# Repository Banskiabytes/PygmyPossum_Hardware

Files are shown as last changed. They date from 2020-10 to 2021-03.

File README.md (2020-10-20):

[][contributors-url]
[][forks-url]
[][stars-url]
[][issues-url]
[][license-url]
[][linkedin-url]

<!-- PROJECT LOGO -->
<br />
<p align="center">
  <a href="https://github.com/tomevison/">
    
  </a>

  <h3 align="center">The Pygmy Possum</h3>
  <p align="center">PIR sensor for camera traps</p>
</p>

<!-- TABLE OF CONTENTS -->
## Table of Contents

* [About the Project](#about-the-project)
* [Built With](#built-with)
* [Usage](#usage)
* [License](#license)
* [Contact](#contact)

<!-- ABOUT THE PROJECT -->
## About The Project

## Built With
#### Software:
* [KiCAD]

<!-- USAGE EXAMPLES -->
## Usage

Set the DIP switches on the front of the board to select your pre-programmed package. There are 8 pre-progammed packages in total. Each package contains a value for:
* Number of Shots to take after a Event
* Time Between Shots
* Minimum time between Events

<!-- LICENSE -->
## License

Distributed under the MIT License. See `LICENSE` for more information.

<!-- CONTACT -->
## Contact

* Tom Evison - tom@evisonengineering.com.au
* James Lidsey - james.lidsey93@gmail.com

<!-- MARKDOWN LINKS & IMAGES -->
<!-- https://www.markdownguide.org/basic-syntax/#reference-style-links -->
[contributors-shield]: https://img.shields.io/github/contributors/tomevison/repo.svg?style=flat-square
[contributors-url]: https://github.com/tomevison/PYGMY/graphs/contributors
[forks-shield]: https://img.shields.io/github/forks/tomevison/repo.svg?style=flat-square
[forks-url]: https://github.com/tomevison/repo/network/members
[stars-shield]: https://img.shields.io/github/stars/tomevison/repo.svg?style=flat-square
[stars-url]: https://github.com/tomevison/repo/stargazers
[issues-shield]: https://img.shields.io/github/issues/tomevison/repo.svg?style=flat-square
[issues-url]: https://github.com/EmbeddedEnvironmental/PygmyPossum_Firmware/issues
[license-shield]: https://img.shields.io/github/license/tomevison/repo.svg?style=flat-square
[license-url]: https://github.com/EmbeddedEnvironmental/PygmyPossum_Firmware/blob/master/LICENSE
[linkedin-shield]: https://img.shields.io/badge/-LinkedIn-black.svg?style=flat-square&logo=linkedin&colorB=555
[linkedin-url]: https://www.linkedin.com/in/thomas-evison-87b27073/# Hardware

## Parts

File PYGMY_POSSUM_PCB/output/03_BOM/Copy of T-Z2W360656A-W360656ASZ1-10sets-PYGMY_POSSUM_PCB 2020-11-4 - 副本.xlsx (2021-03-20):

PYGMY POSSUM v1.1 Build Of Materials
Date: | 2020-11-04
Ref | Value | Part | Footprint | Description | LCSC | Manufacturer | MPN | Package | Type | Part PCBWay Will Supply | Unit Price 10sets | Total Price | PCBWay Comments | Tom Comments
C1 | 0.1uF | Device:C_Small | Capacitor_SMD:C_0603_1608Metric | Unpolarized capacitor, small symbol | C14663 |  |  | 603 | SMD | CC0603KRX7R9BB104 | $0.052 | $0.525
C2 | 10pF | Device:C_Small | Capacitor_SMD:C_0603_1608Metric | Unpolarized capacitor, small symbol | C1634 |  |  | 603 | SMD | CL10C100JB8NNNC | $0.032 | $0.315
C3 | 10pF | Device:C_Small | Capacitor_SMD:C_0603_1608Metric | Unpolarized capacitor, small symbol | C1634 |  |  | 603 | SMD | CL10C100JB8NNNC | $0.032 | $0.315
C4 | CP10u | Device:CP | Capacitor_SMD:CP_Elec_4x3.9 | Polarized capacitor | C134721 |  |  | SMD-ECAP-4x5.3 | SMD | VE-100M1ETR-0405 | $0.210 | $2.100
C5 | CP10u | Device:CP | Capacitor_SMD:CP_Elec_4x3.9 | Polarized capacitor | C134721 |  |  | SMD-ECAP-4x5.3 | SMD | VE-100M1ETR-0405 | $0.210 | $2.100
C6 | 0.1uF | Device:C | Capacitor_SMD:C_0603_1608Metric | Unpolarized capacitor | C14663 |  |  | 603 | SMD | CC0603KRX7R9BB104 | $0.052 | $0.525
D3 | BAT60B | Diode:BAT60A | Diode_SMD:D_SOD-323 | 10V 3A High Current Recitifier Schottky Diode, SOD-323 | C514095 |  |  | SOD-323 | SMD | BAT60B | $0.105 | $1.050
J2 | AudioJack | Connector:AudioJack3 | Connector_Audio:Jack_3.5mm_CUI_SJ-3523-SMT_Horizontal | Audio Jack, 3 Poles (Stereo / TRS) |  | CUI Devices | SJ-3523-SMT-TR |  | SMD |  |  |  |  | This part has been updated (19/11/2020)
J3 | USB_B_Micro | Connector:USB_B_Micro | Connector_USB:USB_Micro-B_Molex-105017-0001 | USB Micro Type B connector |  | Molex | 105017-0001 |  | PTH / SMD | 105017-0001 | $0.945 | $9.450 | 5-7work days
Q1 | 2N7002 | Transistor_FET:2N7002 | Package_TO_SOT_SMD:SOT-23 | 0.115A Id, 60V Vds, N-Channel MOSFET, SOT-23 | C8545 | Changjiang Electronics Tech (CJ) | 2N7002 | SOT-23 | SMD | 2N7002 | $0.105 | $1.050
Q2 | 2N7002 | Transistor_FET:2N7002 | Package_TO_SOT_SMD:SOT-23 | 0.115A Id, 60V Vds, N-Channel MOSFET, SOT-23 | C8545 | Changjiang Electronics Tech (CJ) | 2N7002 | SOT-23 | SMD | 2N7002 | $0.105 | $1.050
Q3 | AO3401A | Transistor_FET:AO3401A | Package_TO_SOT_SMD:SOT-23 | -4.0A Id, -30V Vds, P-Channel MOSFET, SOT-23 | C15127 | Alpha & Omega Semicon | AO3401A | SOT-23 | SMD | AO3401A | $0.210 | $2.100
Q4 | AO3401A | Transistor_FET:AO3401A | Package_TO_SOT_SMD:SOT-23 | -4.0A Id, -30V Vds, P-Channel MOSFET, SOT-23 | C15127 | Alpha & Omega Semicon | AO3401A | SOT-23 | SMD | AO3401A | $0.210 | $2.100
Q5 | 2N7002 | Transistor_FET:2N7002 | Package_TO_SOT_SMD:SOT-23 | 0.115A Id, 60V Vds, N-Channel MOSFET, SOT-23 | C8545 | Changjiang Electronics Tech (CJ) | 2N7002 | SOT-23 | SMD | 2N7002 | $0.105 | $1.050
Q6 | 2N7002 | Transistor_FET:2N7002 | Package_TO_SOT_SMD:SOT-23 | 0.115A Id, 60V Vds, N-Channel MOSFET, SOT-23 | C8545 | Changjiang Electronics Tech (CJ) | 2N7002 | SOT-23 | SMD | 2N7002 | $0.105 | $1.050
R1 | 10K | Device:R | Resistor_SMD:R_0805_2012Metric | Resistor | C17414 | - |  | 805 | SMD | 0805W8F1002T5E | $0.032 | $0.315
R10 | 47K | Device:R | Resistor_SMD:R_0805_2012Metric | Resistor | C17713 | - |  | 805 | SMD | 0805W8F4702T5E | $0.032 | $0.315
R11 | 47K | Device:R | Resistor_SMD:R_0805_2012Metric | Resistor | C17713 | - |  | 805 | SMD | 0805W8F4702T5E | $0.032 | $0.315
R12 | 1M | Device:R | Resistor_SMD:R_0805_2012Metric | Resistor | C17514 | - |  | 805 | SMD | 0805W8F1004T5E | $0.032 | $0.315
R13 | 47K | Device:R | Resistor_SMD:R_0805_2012Metric | Resistor | C17713 | - |  | 805 | SMD | 0805W8F4702T5E | $0.032 | $0.315
R14 | 10K | Device:R | Resistor_SMD:R_0805_2012Metric | Resistor | C17414 | - |  | 805 | SMD | 0805W8F1002T5E | $0.032 | $0.315
R15 | 100K | Device:R | Resistor_SMD:R_0805_2012Metric | Resistor | C17407 | - |  | 805 | SMD |  | $0.032 | $0.315 | Original part is not available, substitute we will supply is 0805W8F1003T5E | this is good
R16 | 10K | Device:R | Resistor_SMD:R_0805_2012Metric | Resistor | C17414 | - |  | 805 | SMD | 0805W8F1002T5E | $0.032 | $0.315
R4 | 1K | Device:R | Resistor_SMD:R_0805_2012Metric | Resistor | C17513 | - |  | 805 | SMD | 0805W8F4702T5E | $0.032 | $0.315
R5 | 1K | Device:R | Resistor_SMD:R_0805_2012Metric | Resistor | C17513 | - |  | 805 | SMD | 0805W8F4702T5E | $0.032 | $0.315
R6 | 1K | Device:R | Resistor_SMD:R_0805_2012Metric | Resistor | C17513 | - |  | 805 | SMD | 0805W8F4702T5E | $0.032 | $0.315
R7 | 10K | Device:R | Resistor_SMD:R_0805_2012Metric | Resistor | C17414 | - |  | 805 | SMD | 0805W8F1002T5E | $0.032 | $0.315
R8 | 1K | Device:R | Resistor_SMD:R_0805_2012Metric | Resistor | C17513 | - |  | 805 | SMD | 0805W8F4702T5E | $0.032 | $0.315
R9 | 1M | Device:R | Resistor_SMD:R_0805_2012Metric | Resistor | C17514 | - |  | 805 | SMD | 0805W8F1004T5E | $0.032 | $0.315
SW1 | SW_DIP_x04 | Switch:SW_DIP_x04 | Button_Switch_SMD:SW_DIP_SPSTx04_Slide_6.7x11.72mm_W8.61mm_P2.54mm_LowProfile | 4x DIP Switch, Single Pole Single Throw (SPST) switch, small symbol |  | MULTICOMP PRO | MCDM(R)-04-T |  | SMD | MCDM(R)-04-T | $1.155 | $11.550 | 5-7work days
SW2 | SW_SPST | Switch:SW_SPST | Button_Switch_THT:SW_CuK_JS202011AQN_DPDT_Angled | Single Pole Single Throw (SPST) switch |  | C & K COMPONENTS | JS202011AQN |  | PTH | JS202011AQN | $0.735 | $7.350
U1 | PIC16F18344-SO | BANKSIA_BYTES_SYMBOLS:PIC16F18344-SOIC | Package_SO:SSOP-20_5.3x7.2mm_P0.65mm | 4096W FLASH, 512B RAM, 256B EEPROM, SOIC-20 | C144347 | MICROCHIP | PIC16F18344-E/SS |  | SMD | PIC16F18344-E/SS | $1.365 | $13.650 | 5-7work days
U2 | CH340G | BANKSIA_BYTES_SYMBOLS:CH340G | Package_SO:SOIC-16_3.9x9.9mm_P1.27mm | USB serial converter, UART, SOIC-16 | C14267 | Jiangsu Qin Heng | CH340G | SOIC-16 | SMD | CH340G | $0.525 | $5.250
U3 | PS2501-1 | BANKSIA_BYTES_SYMBOLS:PS2501-1 | Package_SO:SOIC-4_4.55x2.6mm_P1.27mm | DC Optocoupler, Vce 80V, SOP4 | C51825 | RENESAS |  | Package_SO:SOIC-4_4.55x2.6mm_P1.27mm | SMD | PS2501L-1-F3-A | $0.420 | $4.200
U4 | IP4220CZ6 | BANKSIA_BYTES_SYMBOLS:IP4220CZ6 | BANKSIA_BYTES_FOOTPRINTS:SOT457 | Dual USB 2.0 integrated ESD protection | C282546 | Nexperia | IP4220CZ6,125 | SOT457 | SMD | IP4220CZ6,125 | $0.210 | $2.100
U5 | PS2501-1 | BANKSIA_BYTES_SYMBOLS:PS2501-1 | Package_SO:SOIC-4_4.55x2.6mm_P1.27mm | DC Optocoupler, Vce 80V, SOP4 | C51825 | RENESAS |  | Package_SO:SOIC-4_4.55x2.6mm_P1.27mm | SMD | PS2501L-1-F3-A | $0.420 | $4.200
U6 | AMS1117-3.3 | Regulator_Linear:AMS1117-3.3 | Package_TO_SOT_SMD:SOT-223-3_TabPin2 | 1A Low Dropout regulator, positive, 3.3V fixed output, SOT-223 | C6186 |  |  | SOT-223-3 | SMD | AMS1117-3.3 | $0.210 | $2.100
Y1 | 12MHz | Device:Crystal_GND2_Small | Crystal:Crystal_SMD_3225-4Pin_3.2x2.5mm | Three pin crystal, GND on pin 2, small symbol | C9002 |  |  | SMD-3225_4P | SMD | X322512MSB4SI | $0.210 | $2.100
 |  |  |  |  |  |  |  |  |  |  |  | $81.690

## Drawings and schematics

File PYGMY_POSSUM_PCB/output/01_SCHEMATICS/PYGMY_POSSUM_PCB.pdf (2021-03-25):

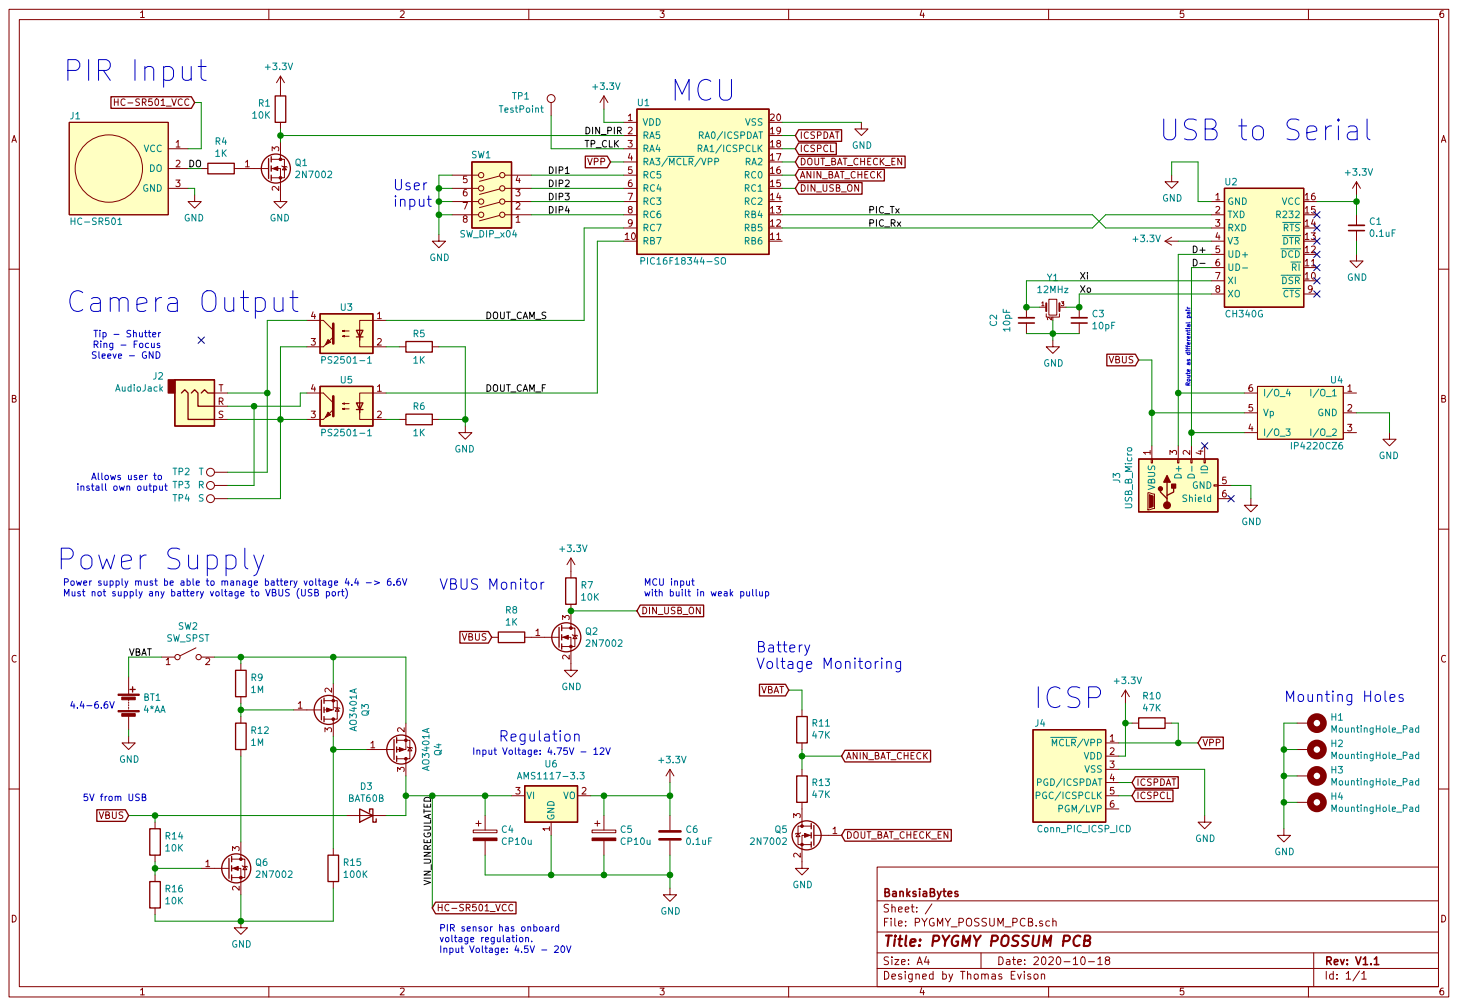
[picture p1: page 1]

Power supply must be able to manage battery voltage 4.4 -> 6.6V
Must not supply any battery voltage to VBUS (USB port)

with built in weak pullup VBUS Monitor

2 3 Q3 AO3401A MCLR/VPP 1 VDD 2 VSS 3 PGD/ICSPDAT 4 PGC/ICSPCLK 5 PGM/LVP 6

File: PYGMY_POSSUM_PCB.sch Sheet: / BanksiaBytes

HC-SR501_VCC
PIR sensor has onboard
voltage regulation.
Input Voltage: 4.5V - 20V

Id: 1/1 Title: PYGMY POSSUM PCB

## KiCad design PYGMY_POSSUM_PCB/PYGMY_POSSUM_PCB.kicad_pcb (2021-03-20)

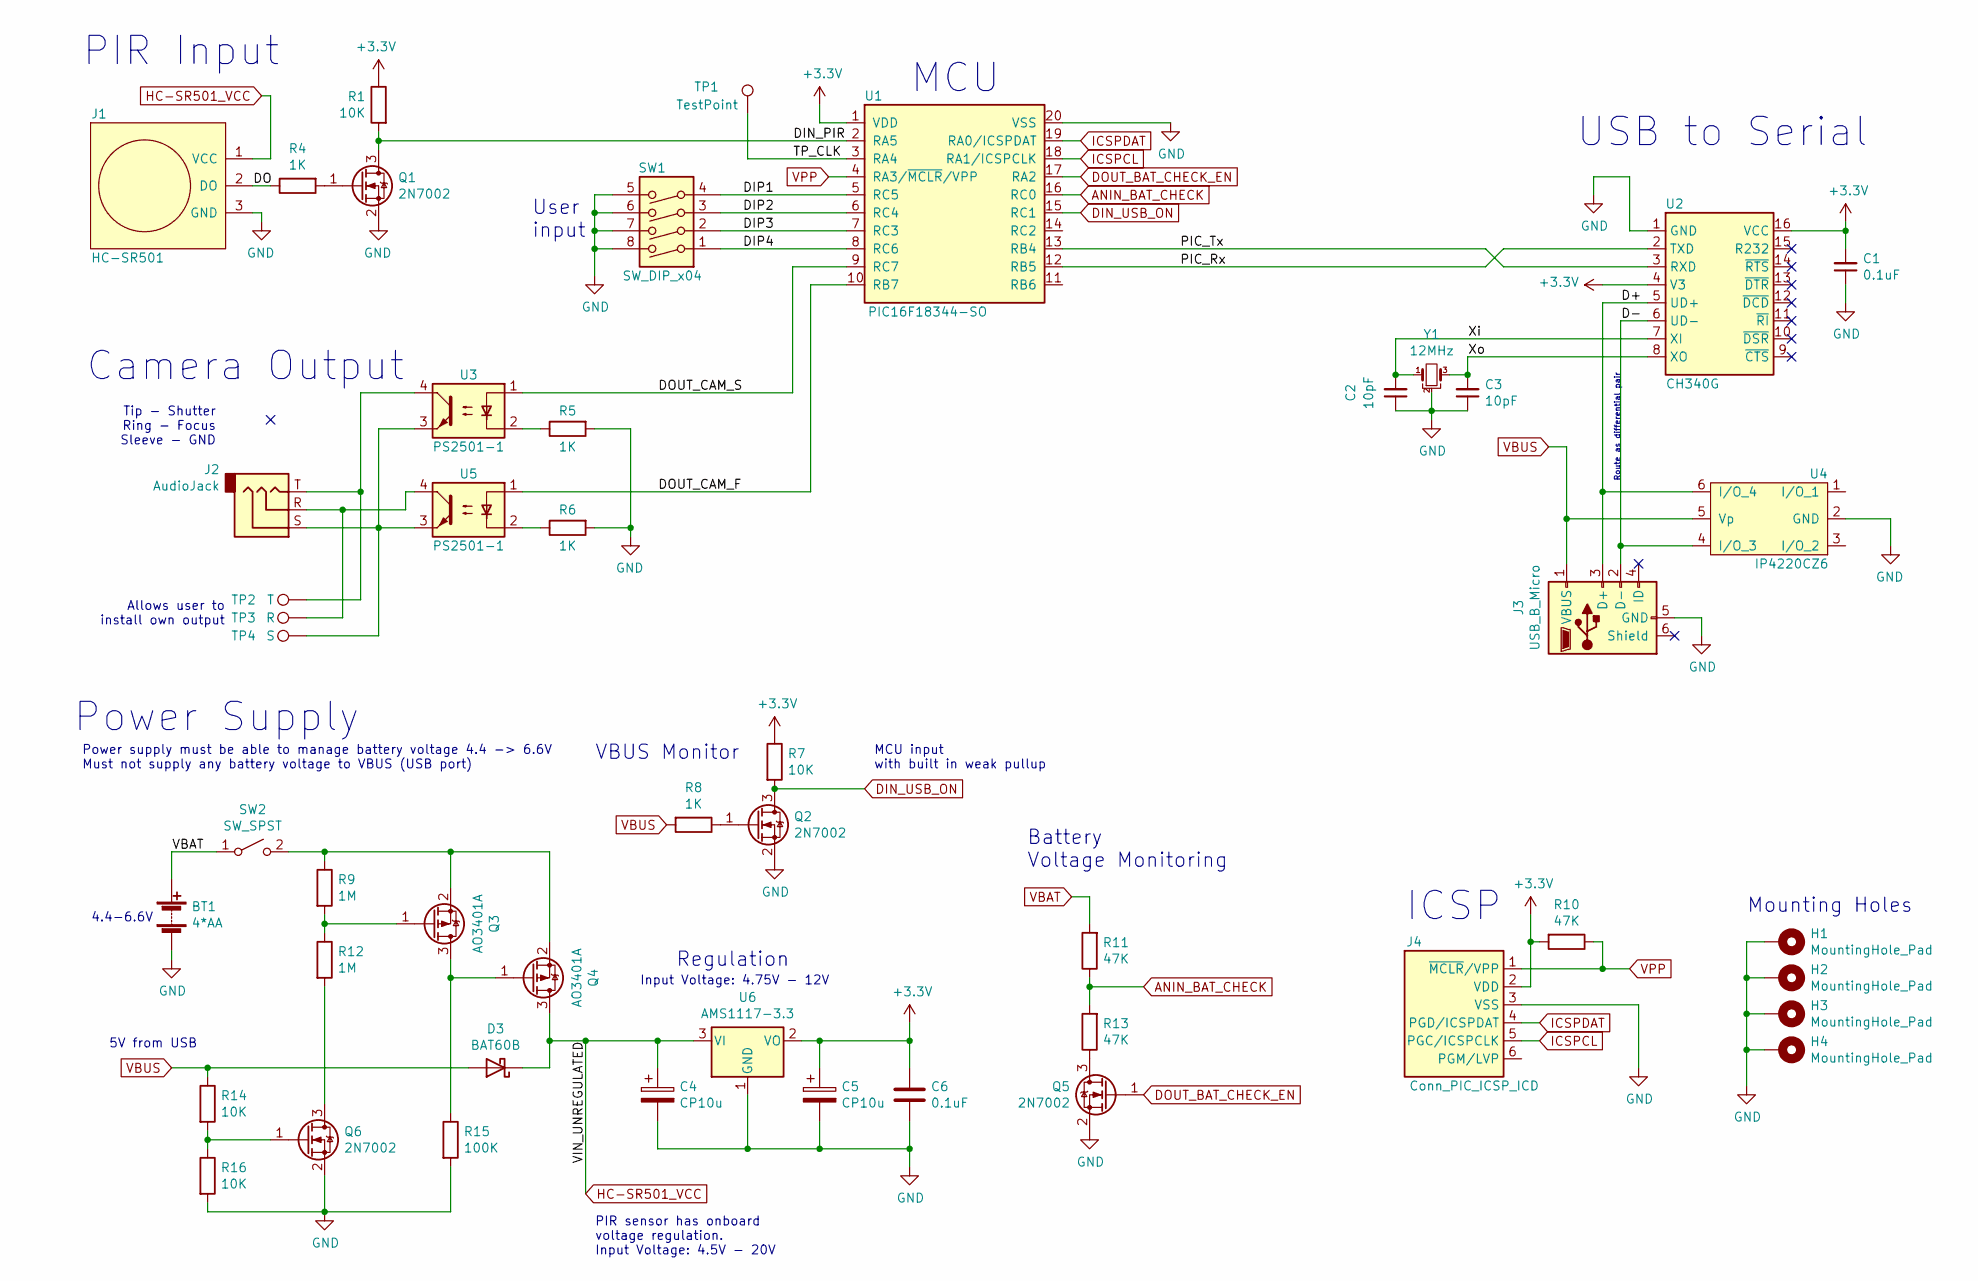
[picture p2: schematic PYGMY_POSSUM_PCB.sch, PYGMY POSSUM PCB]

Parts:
BT1: 4*AA; BatteryHolder_Keystone_2462_2xAA; MPN 2477
C1, C6: 0.1uF; C_0603_1608Metric; LCSC C14663
C2, C3: 10pF; C_0603_1608Metric; LCSC C1634
C4, C5: CP10u; CP_Elec_4x3.9; LCSC C134721
D3: BAT60B; D_SOD-323; LCSC C514095
H1, H2, H3, H4: MountingHole_Pad; MountingHole_3mm_Pad_Via
J1: HC-SR501
J2: AudioJack; Jack_3.5mm_CUI_SJ-3523-SMT_Horizontal; MPN SJ-3523-SMT-TR
J3: USB_B_Micro; USB_Micro-B_Molex-105017-0001; MPN 105017-0001
J4: Conn_PIC_ICSP_ICD; PinHeader_1x06_P2.54mm_Vertical
Q1, Q2, Q5, Q6: 2N7002; SOT-23; MPN 2N7002; LCSC C8545
Q3, Q4: AO3401A; SOT-23; MPN AO3401A; LCSC C15127
R1, R7, R14, R16: 10K; R_0805_2012Metric; LCSC C17414
R4, R5, R6, R8: 1K; R_0805_2012Metric; LCSC C17513
R9, R12: 1M; R_0805_2012Metric; LCSC C17514
R10, R11, R13: 47K; R_0805_2012Metric; LCSC C17713
R15: 100K; R_0805_2012Metric; LCSC C17407
SW1: SW_DIP_x04; SW_DIP_SPSTx04_Slide_6.7x11.72mm_W8.61mm_P2.54mm_LowProfile; MPN MCDM(R)-04-T
SW2: SW_SPST; SW_CuK_JS202011AQN_DPDT_Angled; MPN JS202011AQN
TP1: TestPoint; TestPoint_Pad_D1.0mm
TP2: T; TestPoint_Pad_2.5x2.5mm
TP3: R; TestPoint_Pad_2.5x2.5mm
TP4: S; TestPoint_Pad_2.5x2.5mm
U1: PIC16F18344-SO; SSOP-20_5.3x7.2mm_P0.65mm; MPN PIC16F18344-E/SS; LCSC C144347
U2: CH340G; SOIC-16_3.9x9.9mm_P1.27mm; MPN CH340G; LCSC C14267
U3, U5: PS2501-1; SOIC-4_4.55x2.6mm_P1.27mm; LCSC C51825
U4: IP4220CZ6; SOT457; MPN IP4220CZ6,125; LCSC C282546
U6: AMS1117-3.3; SOT-223-3_TabPin2; LCSC C6186
Y1: 12MHz; Crystal_SMD_3225-4Pin_3.2x2.5mm; LCSC C9002

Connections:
+3V3: C1.2, C5.1, C6.1, J4.2 (VDD), R1.1, R7.1, R10.2, U1.1 (VDD), U2.4 (V3), U2.16 (VCC), U6.2 (VO)
/D+: J3.3 (D+), U2.5 (UD+), U4.6 (I/O_4)
/D-: J3.2 (D-), U2.6 (UD-), U4.4 (I/O_3)
/DIN_PIR: Q1.3 (D), R1.2, U1.2 (RA5)
/DIP1: SW1.4, U1.5 (RC5)
/DIP2: SW1.3, U1.6 (RC4)
/DIP3: SW1.2, U1.7 (RC3)
/DIP4: SW1.1, U1.8 (RC6)
/DO: J1.2 (DO), R4.1
/DOUT_CAM_F: U1.10 (RB7), U5.1
/DOUT_CAM_S: U1.9 (RC7), U3.1
/PIC_Rx: U1.12 (RB5), U2.2 (TXD)
/PIC_Tx: U1.13 (RB4), U2.3 (RXD)
/TP_CLK: TP1.1, U1.3 (RA4)
/Xi: C2.2, U2.7 (XI), Y1.1
/Xo: C3.2, U2.8 (XO), Y1.3
ANIN_BAT_CHECK: R11.1, R13.2, U1.16 (RC0)
DIN_USB_ON: Q2.3 (D), R7.2, U1.15 (RC1)
DOUT_BAT_CHECK_EN: Q5.1 (G), U1.17 (RA2)
GND: BT1.2 (-), C1.1, C2.1, C3.1, C4.2, C5.2, C6.2, H1.1, H2.1, H3.1, H4.1, J1.3 (GND), J3.5 (GND), J4.3 (VSS), Q1.2 (S), Q2.2 (S), Q5.2 (S), Q6.2 (S), R5.2, R6.2, R15.2, R16.2, SW1.5, SW1.6, SW1.7, SW1.8, U1.20 (VSS), U2.1 (GND), U4.2 (GND), U6.1 (GND), Y1.2
HC-SR501_VCC: C4.1, D3.1 (K), J1.1 (VCC), Q4.3 (D), U6.3 (VI)
ICSPCL: J4.5 (PGC/ICSPCLK), U1.18 (RA1/ICSPCLK)
ICSPDAT: J4.4 (PGD/ICSPDAT), U1.19 (RA0/ICSPDAT)
unnamed: J2.R, TP3.1, U5.4
unnamed: J2.S, TP4.1, U3.3, U5.3
unnamed: J2.T, TP2.1, U3.4
unnamed: Q1.1 (G), R4.2
unnamed: Q2.1 (G), R8.1
unnamed: Q3.1 (G), R9.2, R12.1
unnamed: Q3.2 (S), Q4.2 (S), R9.1, SW2.2 (B)
unnamed: Q3.3 (D), Q4.1 (G), R15.1
unnamed: Q5.3 (D), R13.1
unnamed: Q6.1 (G), R14.2, R16.1
unnamed: Q6.3 (D), R12.2
unnamed: R5.1, U3.2
unnamed: R6.1, U5.2
VBAT: BT1.1 (+), R11.2, SW2.1 (A)
VBUS: D3.2 (A), J3.1 (VBUS), R8.2, R14.1, U4.5 (Vp)
VPP: J4.1 (~MCLR~/VPP), R10.1, U1.4 (RA3/~MCLR~/VPP)

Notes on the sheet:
ICSP
Tip - Shutter Ring - Focus Sleeve - GND
Camera Output
USB to Serial
Battery Voltage Monitoring
PIR Input
User input
Route as differential pair
MCU
Mounting Holes
Power supply must be able to manage battery voltage 4.4 -> 6.6V Must not supply any battery voltage to VBUS (USB port)
Power Supply
PIR sensor has onboard voltage regulation. Input Voltage: 4.5V - 20V
4.4-6.6V
Input Voltage: 4.75V - 12V
Regulation
5V from USB
MCU input with built in weak pullup
VBUS Monitor
Allows user to install own output

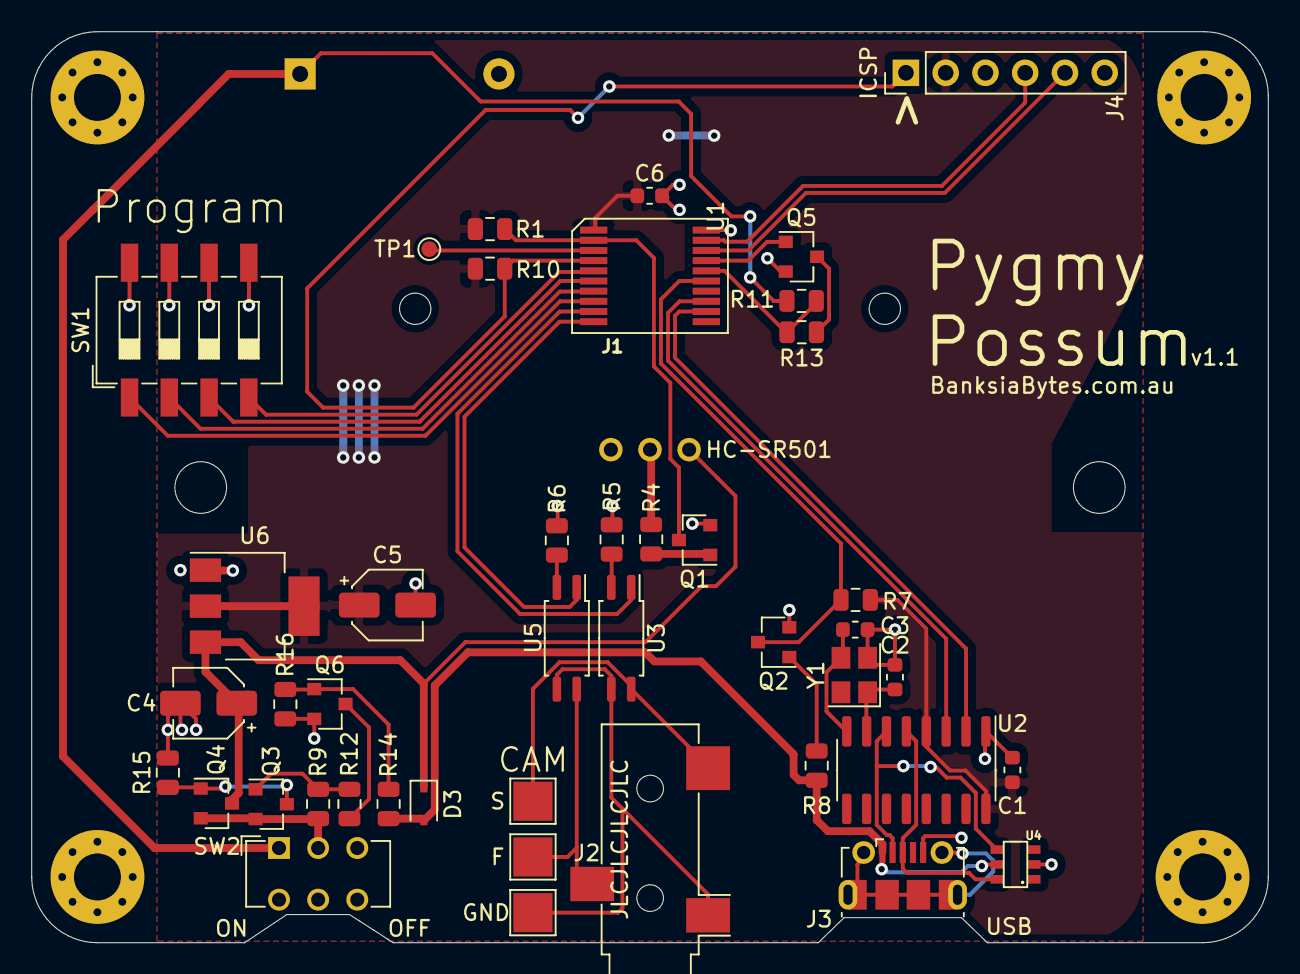
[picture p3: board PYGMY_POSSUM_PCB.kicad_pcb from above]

Board: 2 copper layers, 79.0 x 58.2 mm, 49 parts (1 on the bottom side), 39 nets.

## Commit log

2020-10-19 added bulk of components
    [PYGMY_POSSUM_PCB.sch, file5FA71AB2.sch]
2020-10-20 Added OR logic to power supply. Added all external devices Upgraded MCU to PIC16F18344 to allow for aditional IO.
    [PYGMY_POSSUM_PCB.kicad_pcb, PYGMY_POSSUM_PCB.sch, file5FA71AB2.sch]
